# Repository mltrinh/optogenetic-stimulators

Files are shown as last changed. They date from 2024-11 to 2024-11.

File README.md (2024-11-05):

# Optogenetic Stimulators
Martin Trinh Bioengineering 2024 Capstone. This project aimed to create new optogenetic stimulator boxes for the Moritz Lab to control LED spinal cord implants.

# Optogenetic Stimulator Usage
A picture of the finished box is shown below. 

On the left is a front view picture of the box. To control an LED optogenetic implant, insert the LED anode wire into the **upper** red socket and LED cathode wire into the **upper** black socket. The **lower** red and black sockets can be used to plug in thermistor wires if applicable. *Note: The order the thermistor is plugged in does not matter.*

On the right is a top view picture of the box. The OLED monitor displays the voltage that is sent to the LED Driver (correlated with LED Intensity) and temperature if applicable.
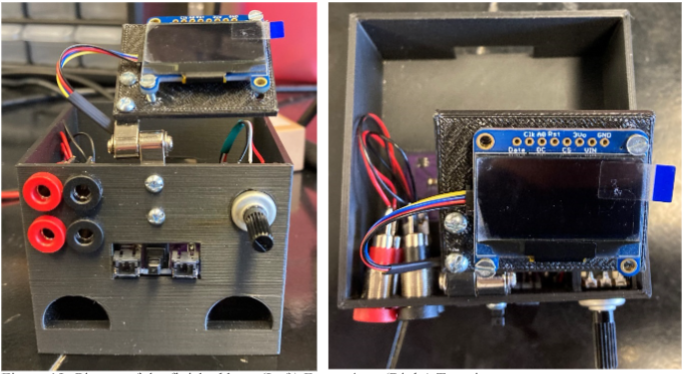
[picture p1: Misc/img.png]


# Necessary Materials per Box and Approximate Cost
See table below for necessary materials to construct one optogenetic box. **Ensure that the components bought will fit into the PCB and housing unit. If components do not fit, the files under "PCB Files" and "3D Printing Files" may need to be adjusted accordingly.**

| Name                                          | Quantity | Unit Price | Price per box |
|-----------------------------------------------|:--------:| :---: |:-------------:|
| PCB Board                                     |    1     | $5.33 |     $5.33     |
| Banana Plug                                   |    4     | $1.20 |     $4.80     |
| 500 mA Diode                                  |    1     | $0.36 |     $0.36     |
| 2 A Diode                                     |    1     | $0.45 |     $0.45     |
| N-Channel 60V 30A (Tc) 70W (Tc) TO-220 MOSFET |    1     | $1.45 |     $1.45     |
| 10 uF Capacitor                               |    2     | $0.17 |     $0.34     |
| 0.15 Ohm Resistor 1% Tolerance                |    1     | $0.69 |     $0.69     |
| 100 kOhm Resistor 0.1% Tolerance              |    1     | $0.39 |     $0.39     |
| 1 kOhm Resistor 5% Tolerance                  |    1     | $0.15 |     $0.15     |
| 10 kOhm Potentiometer                         |    1     | $1.61 |     $1.61     |
| AL8860WT-7 LED Driver                         |    1     | $0.68 |     $0.68     |
| 100 uH Inductor                               |    1     | $0.63 |     $0.63     |
| QT PY M0                                      |    1     | $7.50 |     $7.50     |
| JST-PH 2-pin                                  |    2     | $0.75 |     $1.50     |
| 10 Kohm Resistor 1% Tol                       |    1     |$0.10|     $0.10     |
| Hinge                                         |    1     |$3.80|     $3.80     |
| 7 Position Header                             |     2    |$0.62|     $1.24     |
| Push Button Switch DPST                       | 1 |$2.12|     $2.12     |
| PLA                                           | ~80 grams|$0.014/gram|     $1.12     |
| Stemma QT connector                           | 1 | $0.95|     $0.95     |
| OLED Display                                  | 1 | $17.50|    $17.50     |
| Lithium Ion Cylindrical Battery 3.7V 2.2 A    | 2 | $9.95|    $19.90     |
|                                               | | Total Cost |    $72.61     |

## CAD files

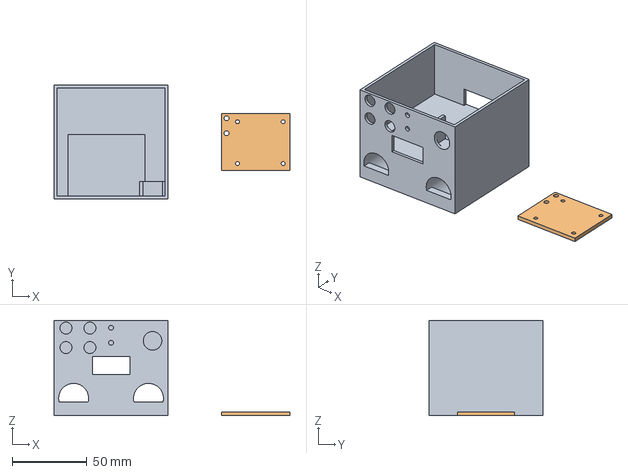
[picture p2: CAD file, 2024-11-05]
3D Printing Files/OLED and Circuit box.3mf
157.6 x 76.2 x 63.5 mm
Circuit box3.STL
OLED display hold.STL

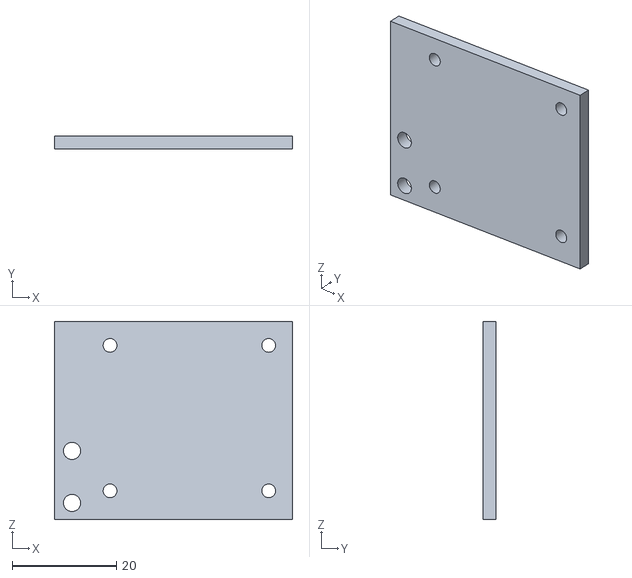
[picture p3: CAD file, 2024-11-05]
3D Printing Files/OLED display hold.STL
45.7 x 2.54 x 38.1

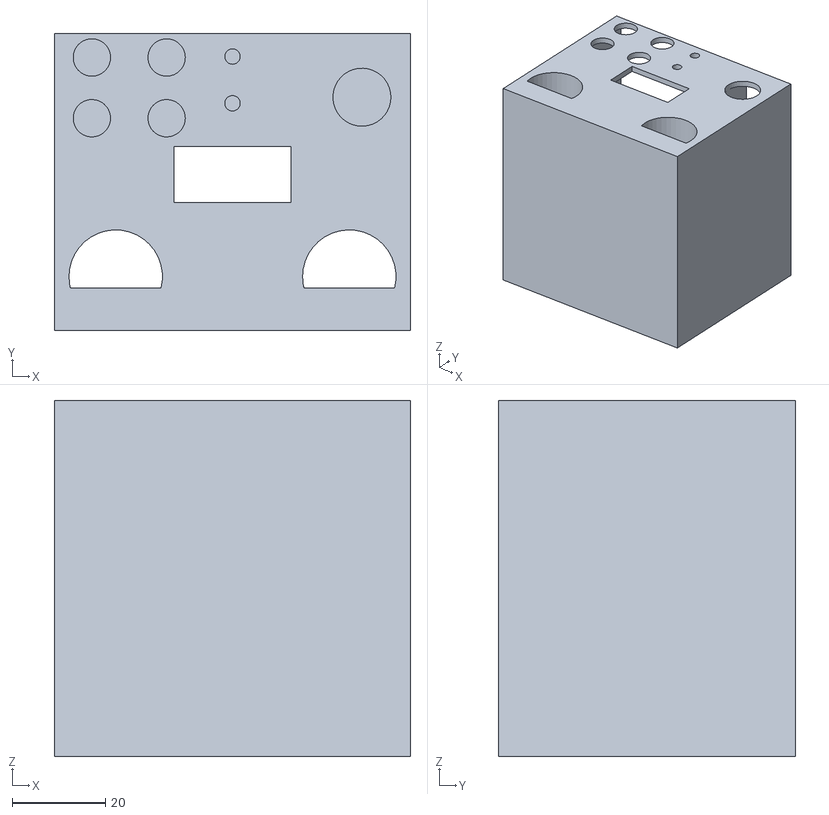
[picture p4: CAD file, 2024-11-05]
3D Printing Files/Circuit box3.STL
76.2 x 63.5 x 76.2

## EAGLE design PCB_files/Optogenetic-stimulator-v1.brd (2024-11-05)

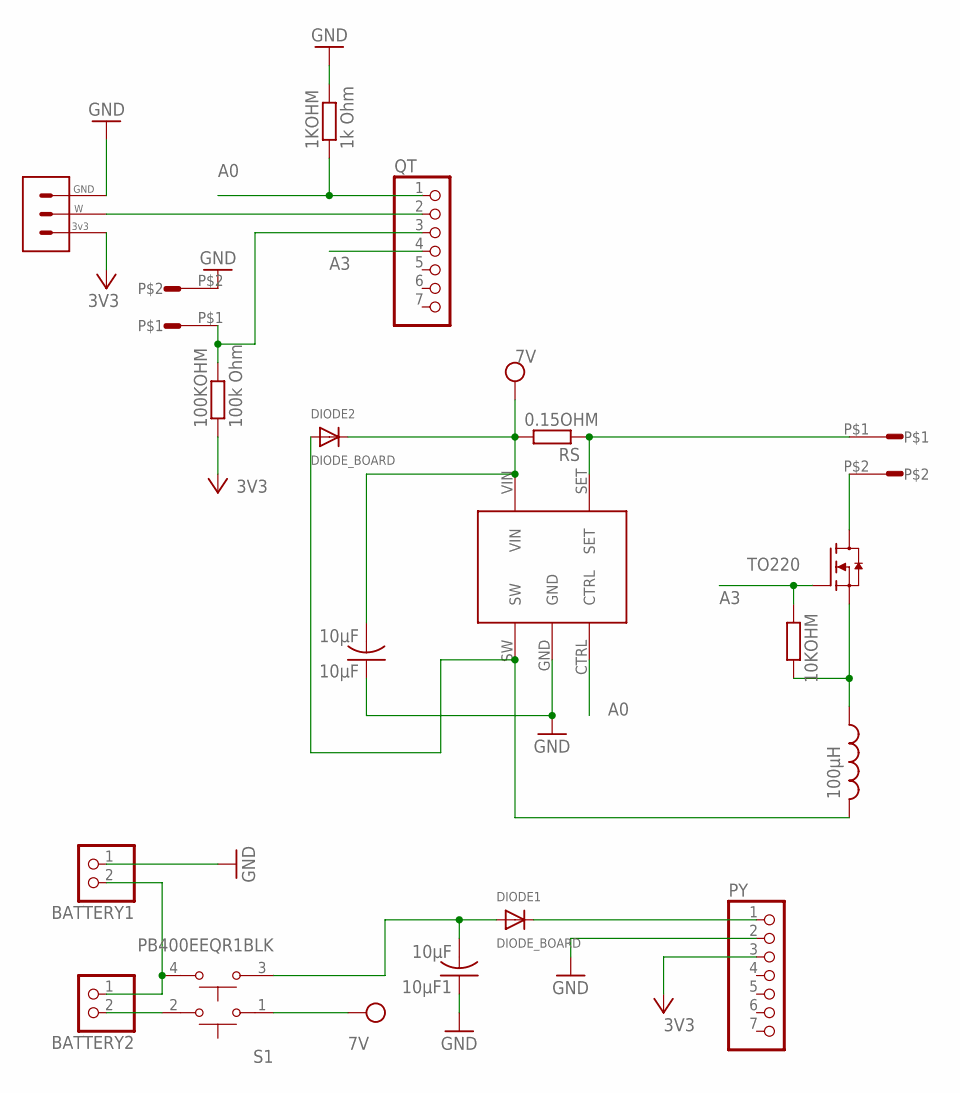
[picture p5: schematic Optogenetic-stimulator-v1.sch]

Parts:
1KOHM: 1k Ohm; M1206
10KOHM: R-EU_M1206; M1206
10µF, 10µF1: 10µF; C1206
100KOHM: 100k Ohm; M1206
AL8860WT1: AL8860WT
BATTERY1, BATTERY2: JST_2PIN-THM; JST-PH-2-THM
DIODE1, DIODE2: DIODE_BOARD; DIODE
LED: UNIVERSAL_PAD
NTC: UNIVERSAL_PAD
PY: PINHD-1X7; 1X07
QT: PINHD-1X7; 1X07
RS: 0.15OHM; M1206
S1: PB400EEQR1BLK; SW_PB400EEQR1BLK
TO220: MOSFET-TO220; TO220
U$1: BOARD_INDUCTOR; INDUCTOR
U$6: POTENTIOMETER_BOARD

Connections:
3V3: 100KOHM.1, PY.3, U$6.3V3
7V: 10µF.2, AL8860WT1.VIN, DIODE2.P$2 (C), RS.2, S1.1
A0: 1KOHM.1, AL8860WT1.CTRL, QT.1
A3: 10KOHM.1, QT.4, TO220.1 (G)
GND: 1KOHM.2, 10µF.1, 10µF1.1, AL8860WT1.GND, BATTERY1.1 (2), NTC.P$2, PY.2, U$6.GND
unnamed: BATTERY1.2 (1), BATTERY2.1 (2), S1.4
unnamed: DIODE1.P$2 (C), PY.1
unnamed: LED.P$2, TO220.2 (D)
unnamed: 10µF1.2, DIODE1.P$1 (A), S1.3
unnamed: 100KOHM.2, NTC.P$1, QT.3
unnamed: BATTERY2.2 (1), S1.2
unnamed: AL8860WT1.SW, DIODE2.P$1 (A), U$1.P$2 (2)
unnamed: QT.2, U$6.W
unnamed: AL8860WT1.SET, LED.P$1, RS.1
unnamed: 10KOHM.2, TO220.3 (S), U$1.P$1 (1)

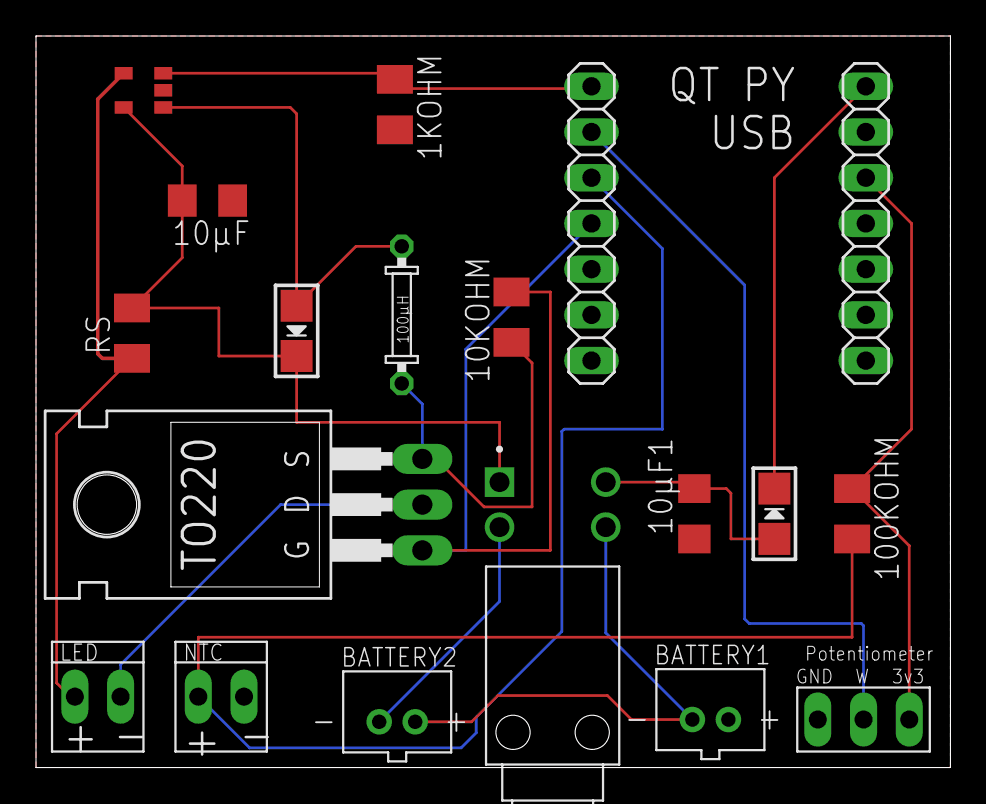
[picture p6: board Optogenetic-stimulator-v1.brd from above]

Board: 2 copper layers, 50.8 x 40.6 mm, 19 parts (0 on the bottom side), 15 nets.

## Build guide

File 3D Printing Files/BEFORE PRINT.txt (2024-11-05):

For new PCB, the battery sockets on the housing unit will need to be changed.

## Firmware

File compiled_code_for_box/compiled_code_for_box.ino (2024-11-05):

// Import Neopixel module (onboard LED) and display modules
#include <Adafruit_NeoPixel.h>
#include <Adafruit_GFX.h>
#include <Adafruit_SSD1306.h>

// Define relevant pins for stim/thermistor readout and moving average buffer size
#define LED_PIN A0
#define POTENTIOMETER_PIN A1
#define THERMISTOR_PIN A2
#define PARADIGM_PIN A3
#define BUFFER_SIZE 10

// Define Display properties
#define SCREEN_ADDRESS 0x3D
#define DISPLAY_WIDTH 128
#define DISPLAY_HEIGHT 64

// Initialize onboard LED and create relevant variables for stimulation
Adafruit_NeoPixel pixels(1, PIN_NEOPIXEL);
unsigned long innerStartTime, outerStartTime, currentTime, update;
const unsigned int pulseWidth_c = 1e6;
const unsigned int period_c = 2e6;
const unsigned int pulseWidth_stim = 5e3;
const unsigned int period_stim = 245e3;
const unsigned int on_stim = 5e6;
const unsigned int off_stim = 20e6;
const unsigned int errorTime = 3.6e9;
int potentiometerBuffer[BUFFER_SIZE];

// Initialize SSD display
Adafruit_SSD1306 display(DISPLAY_WIDTH, DISPLAY_HEIGHT, &Wire);

// Create relevant variables for thermistor
const unsigned int fixed_resistor = 100000;
const float c1 = 0.0013886299, c2 = 0.00013769741, c3 = 2.5665933e-07;
const unsigned int updateTime = 1e6;
int temperatureBuffer[BUFFER_SIZE];
float startingTemp;

void setup() {
  Serial.begin(9600);
  delay(500);

  display.begin(SSD1306_SWITCHCAPVCC, SCREEN_ADDRESS);
  display.clearDisplay();

  pinMode(PARADIGM_PIN, OUTPUT);
  analogReadResolution(12);
  analogWriteResolution(10);

  float startingTemp_V = 0;
  for (int writeIdx = 0; writeIdx < BUFFER_SIZE; writeIdx++) {
    startingTemp_V += analogRead(THERMISTOR_PIN);
  }
  float filtered_startingTemp_V = float(startingTemp_V)/BUFFER_SIZE;
  startingTemp = convertVoltagetoTemp(filtered_startingTemp_V);

  pixels.begin();
  innerStartTime = micros();
  outerStartTime = micros();
}

void loop() {
  currentTime = micros();
  static int writeIdx = 0;

  int potentiometerInput = analogRead(POTENTIOMETER_PIN);
  int temperatureInput = analogRead(THERMISTOR_PIN);

  potentiometerBuffer[writeIdx] = potentiometerInput;
  temperatureBuffer[writeIdx] = temperatureInput;
  writeIdx++;
  writeIdx = (writeIdx >= BUFFER_SIZE) ? 0 : writeIdx;
  long pot_sum = 0;
  long temp_sum = 0;

  for (int i = 0; i < BUFFER_SIZE; i++) {
    pot_sum += potentiometerBuffer[i];
    temp_sum += temperatureBuffer[i];
  }
  int filtered_pot = float(pot_sum)/BUFFER_SIZE;
  float filtered_temp = float(temp_sum)/BUFFER_SIZE;

  //potentiometerInput = map(potentiometerInput, 0, 4095, 0, 460); //500 => 340 -> 315 mW; 460 => 300 -> 275 mW was on 350
  filtered_pot = map(filtered_pot, 0, 4095, 0, 350);
  float output_A0 = filtered_pot * (3.3/1023);
  if (currentTime <= errorTime) {
    pixels.setPixelColor(0, pixels.Color(0, 0, 255));
    beginCallibration();
    //beginStimulation();
    analogWrite(LED_PIN, filtered_pot);
  } else {
    pixels.setPixelColor(0, pixels.Color(255, 0, 0));
    beginCallibration();
    analogWrite(LED_PIN, 0);
  }
  
  //Thermistor Resistor
  float T = convertVoltagetoTemp(filtered_temp);

  if (currentTime >= update) {
    displayVoltage(output_A0);
    displayTemp(T);
    update += updateTime;
  }
}

// Functions used below:
// displayData: Show show relevant information onto SSD display
void displayVoltage(float potentiometer) {
  display.setCursor(0,0);
  display.setTextColor(WHITE, BLACK);
  display.print(F("A0: "));
  display.print(potentiometer);
  display.print(" V");
  display.display();
}

void displayTemp(float temperature) {
  display.setCursor(0,20);
  display.setTextColor(WHITE, BLACK);
  display.print(F("Curr Temp: "));
  display.print(temperature);
  display.print(" C ");
  display.setCursor(0, 40);
  display.print(F("Start Temp: "));
  display.print(startingTemp);
  display.print(" C ");
  display.display();
}

// cyleTiming: start stim paradigm with specified pulsewidth and period/frequency
void cycleTiming(int pulseWidth, int period) {
  if (currentTime - innerStartTime <= pulseWidth) {
    pixels.show();
    digitalWrite(PARADIGM_PIN, HIGH);
  } else {
    pixels.clear();
    pixels.show();
    digitalWrite(PARADIGM_PIN, LOW);
  }

  if (currentTime - innerStartTime >= period) {
    innerStartTime = micros();
  }
}

// beginStimulation: start specific stim paradigm (5 seconds on, 15 seconds off: 4 Hz; 5 ms Pulsewidth)
void beginStimulation() {
  if (currentTime - outerStartTime <= on_stim) {
    cycleTiming(pulseWidth_stim, period_stim);
  } else {
    pixels.clear();
    pixels.show();
    digitalWrite(PARADIGM_PIN, LOW);
  }

  if (currentTime - outerStartTime >= off_stim) {
    outerStartTime = micros();
  }
}

// beginCallibration: start specific stim paradigm (1 second on, 1 second off)
void beginCallibration() {
  cycleTiming(pulseWidth_c, period_c);
}

float convertVoltagetoTemp(float voltage) {
  voltage = (4095 / voltage) - 1;
  float R_th = fixed_resistor / voltage;
  float logR = log(R_th);
  float T = (1.0 / (c1 + c2*logR + c3*logR*logR*logR)) - 273.15;
  return T;
}

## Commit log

2024-11-05 Files to print the 3D housing unit for optogenetic stimulators
    [Circuit box3.STL, OLED and Circuit box.3mf, OLED display hold.STL]
2024-11-05 Arduino IDE code for the QT PY M0 microcontroller
2024-11-05 Files for creating PCB board of optogenetic stimulators
    [Optogenetic-stimulator-v1.brd, Optogenetic-stimulator-v1.sch, Optogenetic-stimulator-v2.brd, Optogenetic-stimulator-v2.sch]
2024-11-05 Included usage and necessary materials section
